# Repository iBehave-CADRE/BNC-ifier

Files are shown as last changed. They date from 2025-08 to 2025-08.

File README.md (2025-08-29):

# BNC-ifier User Guide

The BNC-ifier (Figure 1) adds I/O BNC connectors to Basler cameras, enabling simple integration into experimental imaging and behavioral setups for neuroscience. The PCB is designed to be accessible for scientists, with thorough documentation for self-assembly. Its modular design and detailed instructions allow users to adapt the PCB for any of the supported Basler cameras. A list of supported cameras with connection instructions can be found [here](https://ibehave-cadre.github.io/BNC-ifier).  A full list of parts (Table 1) and manufacturing files are provided in this repository. The BNC-ifier can be used as a stackable device or mounted in 19-inch racks.

<p align="center">
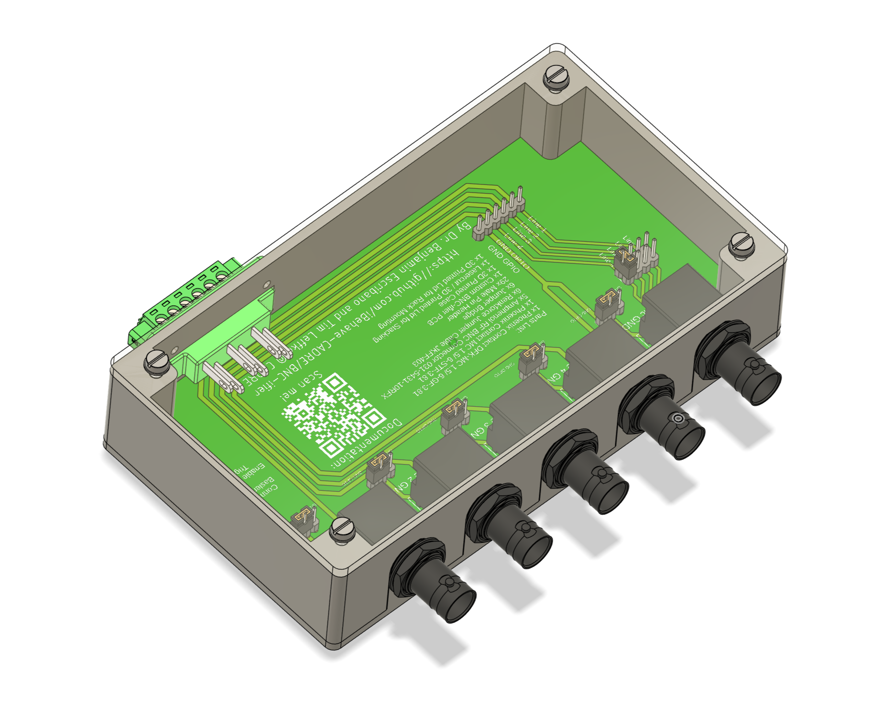
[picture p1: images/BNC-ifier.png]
  
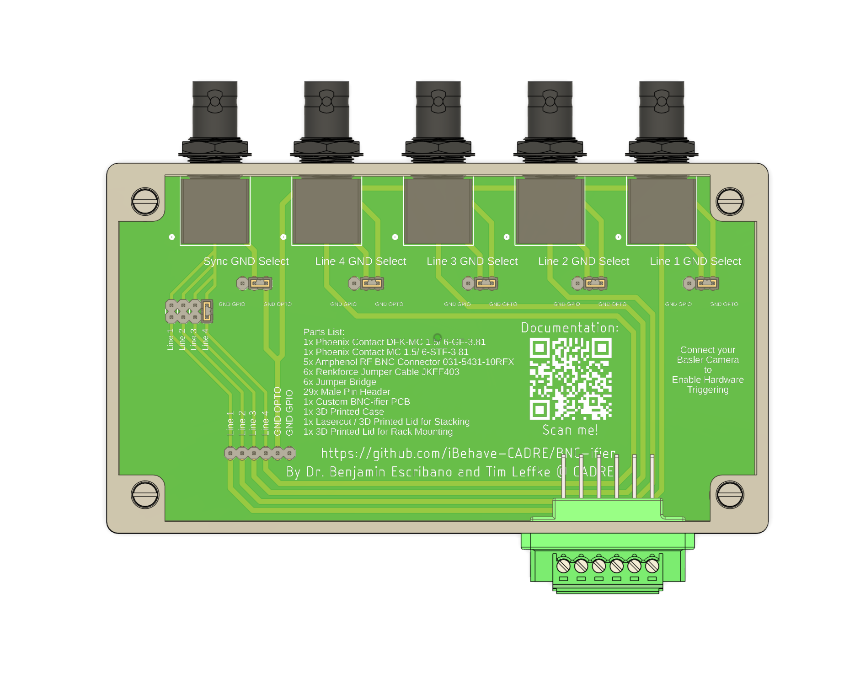
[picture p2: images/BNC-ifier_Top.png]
  
</p>

**Figure 1:** The BNC-ifier (left) and the accessible documentation with parts list, QR code for GitHub and contact details on the PCB (right).

Using this device allows synchronization of the Basler camera with microscopes, DAQs, sensors, and actuators via 5V TTL digital pulses (Figure 2). It also allows daisy-chaining Basler cameras via the sync port in order to synchronize frames between cameras. Additionally, one can grab time stamps from the sync port or one of the many BNC ports, depending on the I/O settings.

<p align="center">
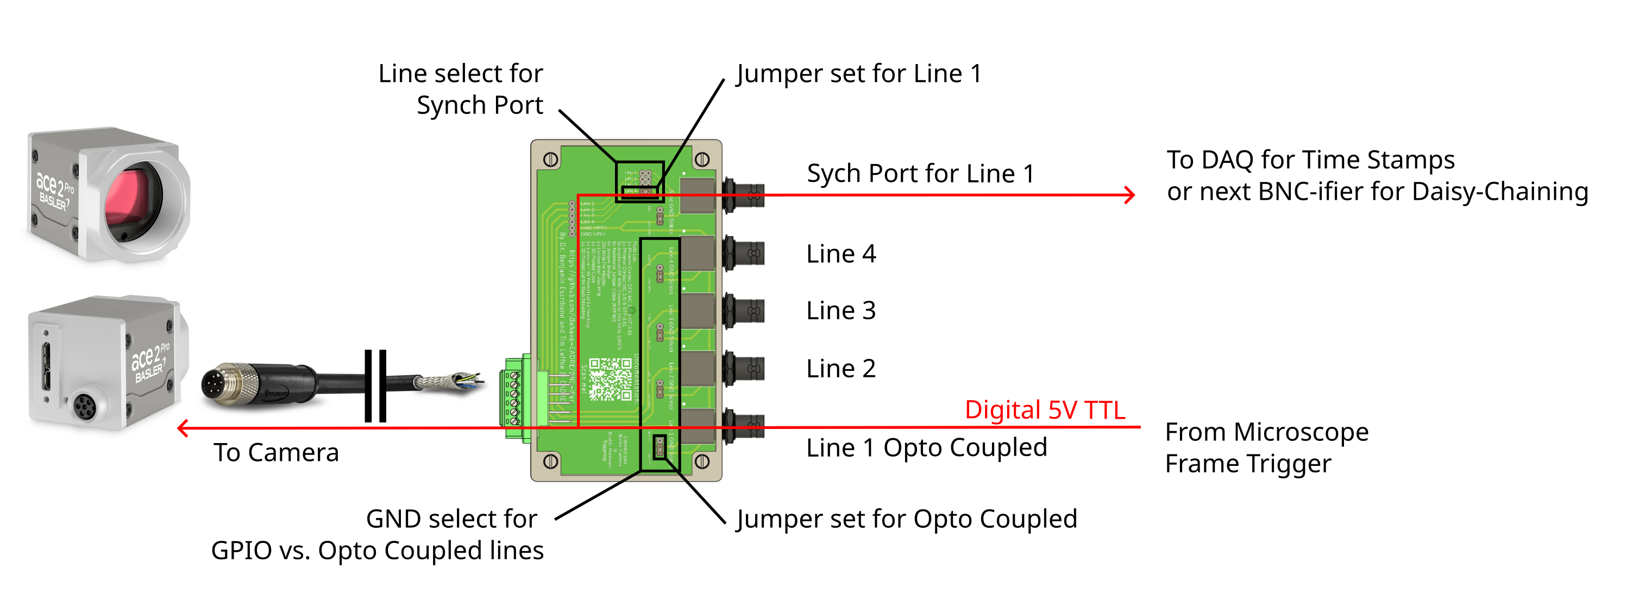
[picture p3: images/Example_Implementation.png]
  
</p>

  **Figure 2:** Schematic of exemplary implementation of the BNC-ifier. Here, a 2P-Microscope frame frigger (e.g. from ScanImage) is connected to Line 1 to trigger individual frames of the Basler camera. At the same time, the sync port is connected to a DAQ for data logging and time stamps. The image of the Basler camera and I/O cable wasobtained and adapted from [baslerweb.com](https://www.baslerweb.com/).

## Assembly

For assembling the BNC-ifier, access to a 3D printer, a laser cutter, and a soldering station are recommended. The PCB can be obtained in the CADRE Maker Space or ordered via any online manufacturer for PCBs. The commercial parts can be ordered online if not available in the CADRE Maker Space. We also provide support for sourcing all the parts and keep them in stock if possible. All parts for the case can be 3D printed in the CADRE Maker Space or ordered via online 3D printing services.

<p align="center">
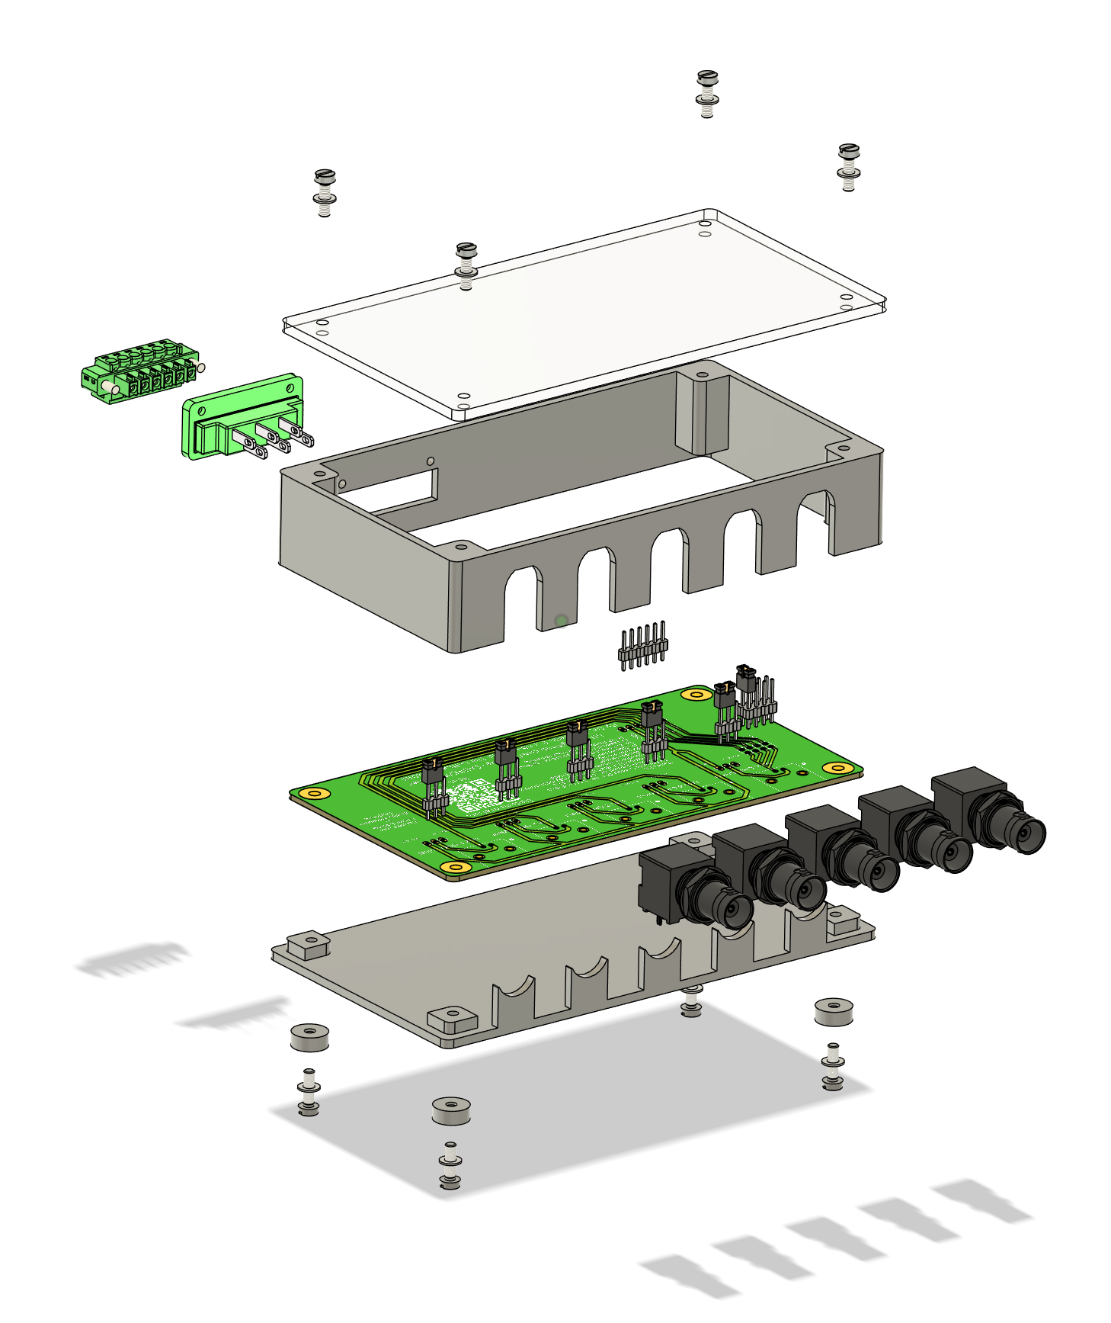
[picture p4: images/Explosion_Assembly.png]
  
</p>

**Figure 3:** Exploded view of the BNC-ifier for assembly instructions.

1. Assembling the PCB: All electronic parts have to be soldered to the top side of the PCB at the labeled positions. This includes the BNC connectors and all the male pin headers. Once all the parts are soldered, each pin terminal can be equipped with a jumper bridge. This jumper will later be used for the configuration of the BNC-ifier.

2. Preparing the Connector: The green Phoenix Contact connector has to be equipped with jumper cables. Therefore, jumper cables with female pin headers have to be soldered to the connector and finished with shrink tubing.

3. Preparing the Case: All parts of the case have to be 3D printed and laser cut. Once they are manufactured, they can be assembled with screws (Figure 3). The PCB goes in between the top and bottom parts of the case. The Phoenix Contact connector then needs to be attached to the hole, and the jumper cables need to be inserted.

5. Now the lid can be closed with the additional screws.

> [!NOTE]
> For the rack-mounted version (Figure 4), the lid needs to be closed after placing the BNC-ifier in the rack panel. Closing the lid will then secure the device in the panel.

<p align="center">
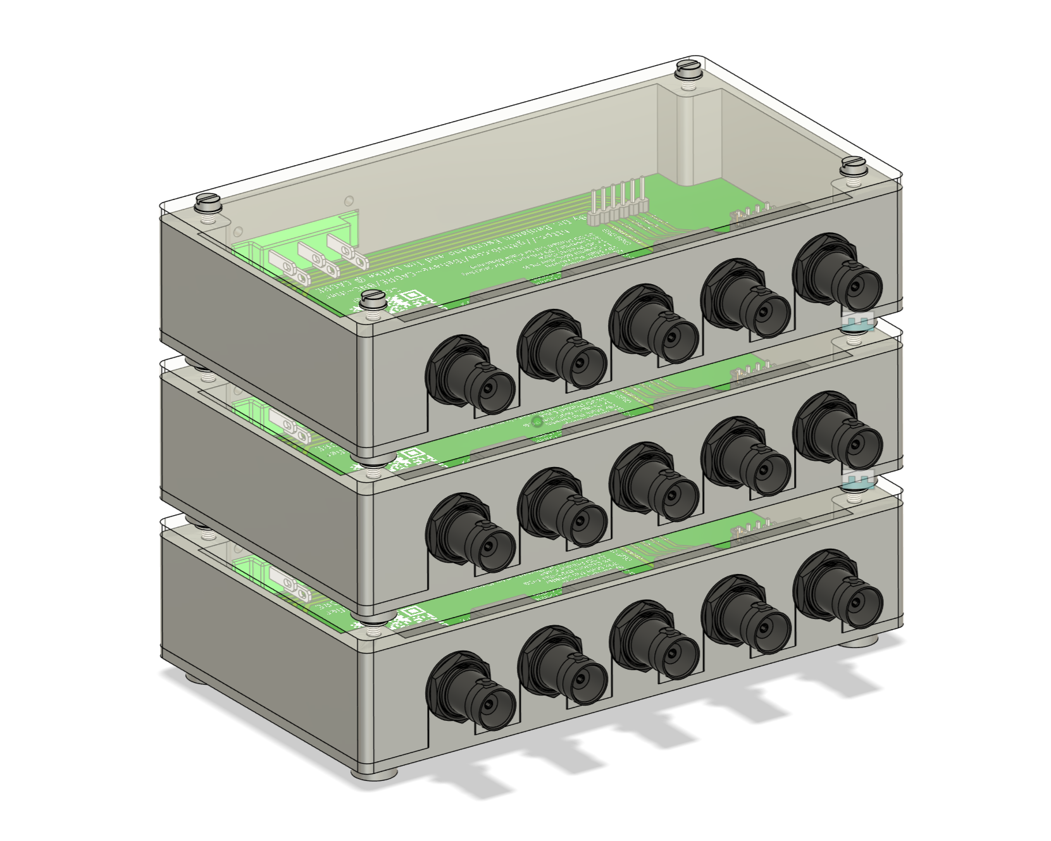
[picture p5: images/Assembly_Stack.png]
  
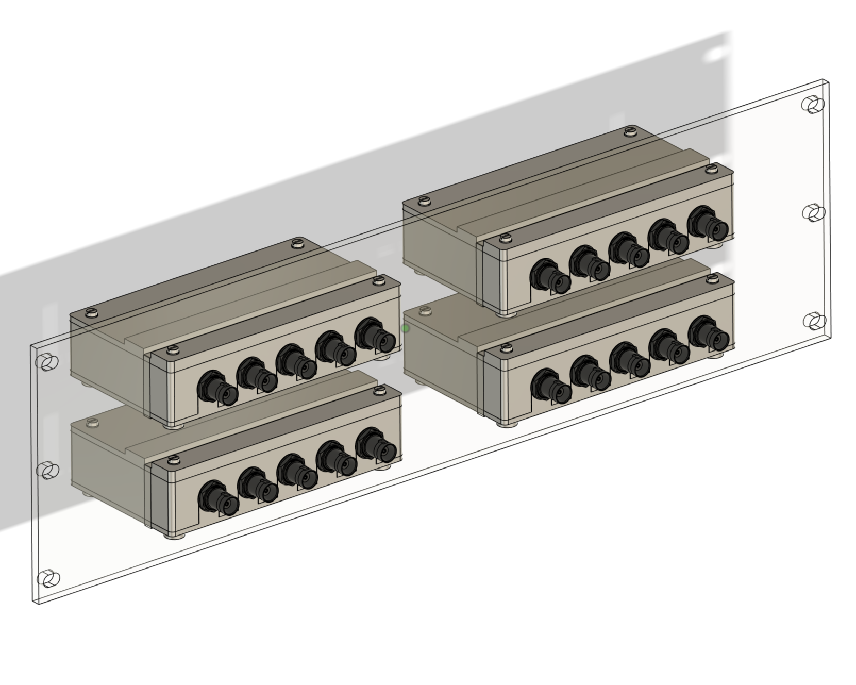
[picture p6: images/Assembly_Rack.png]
  
</p>

**Figure 4:** BNC-ifier as a stack (left) and mounted in a rack panel (right).

## Configuration of the BNC-ifier

For connecting the Basler camera to the BNC-ifier, an I/O cable with the corresponding connector for the camera on one end and open pins on the other end must be available. This cable can be ordered on the Basler web page using the following [link](https://www.baslerweb.com/en/accessories/?accessory_type=I/O+/+Power+Cable#products). Normally, the cable comes with a small piece of paper providing the color code, cable pin layout, and numbering.

> [!TIP]
> If this document was lost or not provided, the color code and pin layout of the cable can be determined with a multimeter in continuity mode. Connecting the probes to a pin of the cable connector and an open wire end of the cable will make the multimeter beep if there is electrical continuity. The pairing of beeping pins and wire colors can then be noted down.

Depending on the camera model, each I/O line can be an opto-coupled or a GPIO line, while each type has its own ground pin. Therefore, the BNC-ifier grounding scheme has to be configured in order to provide each pin with the correct reference ground.

To find out which camera pin has to be connected to which BNC-ifier pin, please refer to this [site](https://ibehave-cadre.github.io/BNC-ifier). Clicking on the camera name will provide the pin type, pin layout, and pin number of each camera, along with an illustration and table. If this site does not work, please refer to the `cameras.csv` file and the `pin_numbering` folder in this repository.

The BNC-ifier can now be configured as follows:

1. Connect each camera pin to the corresponding pin of the Phoenix Contact connector screw terminal on the BNC-ifier box.
2. Unscrew the top of the BNC-ifier and open the lid.
3. Each jumper cable can now be connected to the corresponding line on the 6x male pin header terminal.
3. The jumper bridges on the 3x male pin headers can now be placed to select the corresponding ground (opto-coupled vs. GPIO) for Lines 1-4.

> [!TIP]
> If there is no ground (GND) for the line in the table, it does not matter how the pin header is set.

4. To configure the sync port, the jumper bridge can be placed to select one of the four lines on the 2x4 male pin header. This will allow output of any signal on the selected line to the sync BNC port in a bidirectional manner.
5. Place the lid back on the BNC-ifier and screw it on.

## Integration in Experimental Setups

The BNC-ifier can now be connected to other devices via coaxial BNC cables. Lines 1-4 can be configured in Pylon in order to start camera frames, provide information like exposure time or timestamps, and much more. The sync port can also be used for recording timestamps via a DAQ, but if connected to Lines 1-4 of another camera, it acts as a daisy-chaining port. The provided wiring diagram (Figure 5) and PCB layout (Figure 6) can help to understand the BNC-ifier and plan its setup integration.

## References and Contact Details

The BNC-ifier is used by the laboratories of Sabine Krabbe (DZNE, Bonn), Tobias Rose (IEECR, Bonn), Tobias Ackels (IEECR, Bonn), Ilona Grunwald-Kadow (Institute for Physiology, Bonn), and many more to come...

For any further questions, please contact the [CADRE Team](https://ibehave.nrw/ibots-platform/cadre/)

## Wiring Diagram

<p align="center">
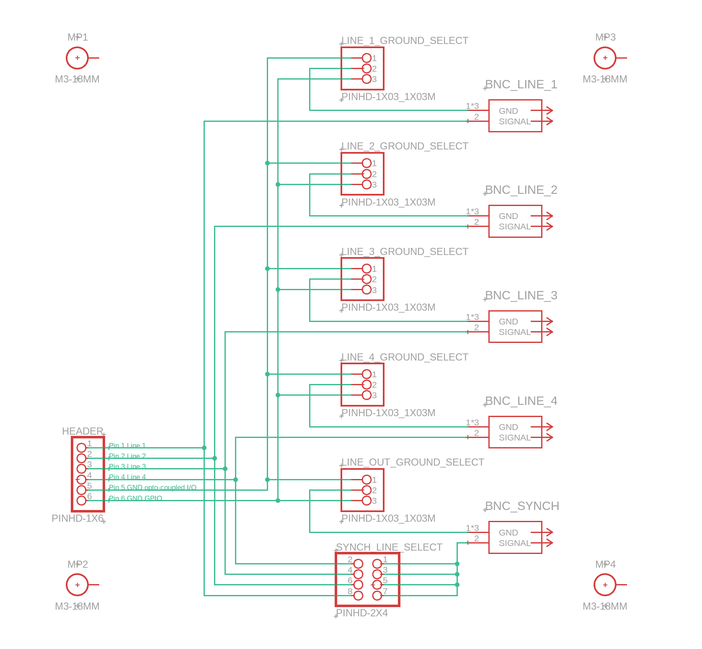
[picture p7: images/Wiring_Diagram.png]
  
</p>

**Figure 5:** Schematics of electronics circuit of the BNC-fier.

## PCB Layout

<p align="center">
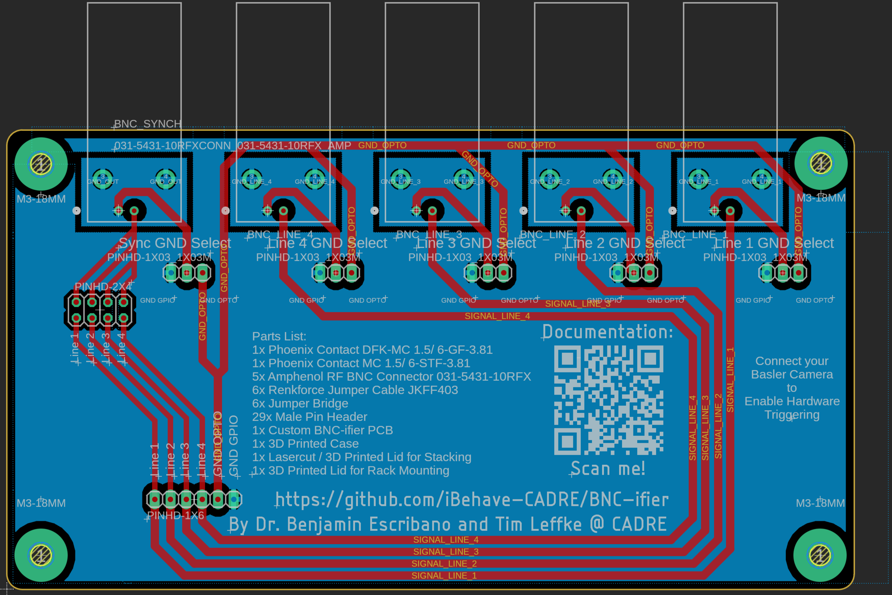
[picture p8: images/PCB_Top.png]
  
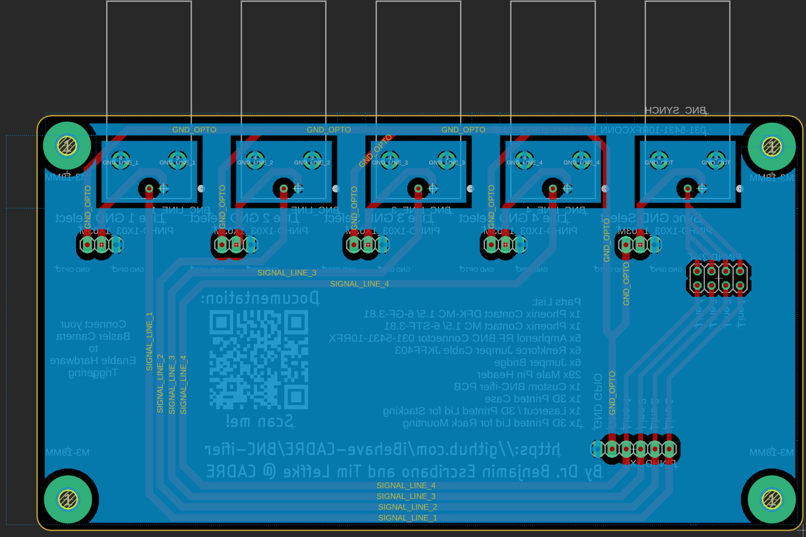
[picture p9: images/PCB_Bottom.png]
  
</p>

**Figure 6:** PCB layout of the BNC-ifier from top (left) and bottom (right).

## Parts List

| Item | Quantity | Notes | Product Example Link |
| :--- | :---: | :---: | :---: |
|  |  |  |  |
| **Commercial Parts:** |
|  |  |  |  |
| Custom BNC-ifier PCB | 1 piece | [custom design](PCB) | [eurocircuits.com](https://www.eurocircuits.com/) |
| Phoenix Contact DFK-MC 1.5/ 6-GF-3.81 | 1 piece | |[rs-online.com](https://uk.rs-online.com/web/p/pluggable-terminal-blocks/1761449?gb=s)|
| Phoenix Contact MC 1.5/ 6-STF-3.81 | 1 piece ||[rs-online.com](https://uk.rs-online.com/web/p/pluggable-terminal-blocks/1703921?gb=s)|
| Amphenol RF BNC Connector 031-5431-10RFX | 5 pieces ||[rs-online.com](https://uk.rs-online.com/web/p/coaxial-connectors/1440890?gb=a)|
| Renkforce Jumper Cable JKFF403 | 6 pieces ||[rs-online.com](https://www.conrad.de/de/p/renkforce-jkff403-jumper-kabel-arduino-banana-pi-raspberry-pi-40x-drahtbruecken-buchse-40x-drahtbruecken-buchse-30-2299845.html)|
| Jumper Bridge | 6 pieces ||[rs-online.com](https://de.rs-online.com/web/p/jumper/7636776P?gb=s)|
| Male Pin Header | 29 pieces ||[rs-online.com](https://de.rs-online.com/web/p/leiterplatten-header/2518632?gb=s)|
| Shrink Tube | 16 pieces of 1.5 cm ||[rs-online.de](https://de.rs-online.com/web/p/warmeschrumpfschlauche/2833249?gb=s)|
| Screw M3x10 Flathead | 8 pieces | self-tapping|[mercateo.com](https://www.mercateo.com/p/1498C-8000152817/Flachkopfschraube_DIN_85_ISO_1580_Schlitz_M3x10_4_8_galv_verz_200St_.html?ViewName=live~secureMode)|
| Washer M3 | 8 pieces | |[mercateo.com](https://www.mercateo.com/p/4502-16H900/Unterlegscheibe_M3_H_0_5_mm_Aussen_7_mm_Stahl_verzinkt_DIN_125_ISO_7090_.html?ViewName=live~secureMode)|
|  |  |  |  |
| **Parts for Case:** |
|  |  |  |  |
| Case Frame Top | 1 piece | [custom design](Case/Case_Frame_Top.stl) | 3D printed |
| Case Frame Bottom | 1 piece | [custom design](Case/Case_Frame_Bottom.stl) | 3D printed |
|  |  |  |  |
| **Parts for Stacking Case:** |
|  |  |  |  |
| Top Lid Stackable | 1 piece | [custom design](Case/Top_Lid_Stackable.stl) | lasercut, can be printed |
| Stacking Feet | 4 pieces | [custom design](Case/Stacking_Feet.stl) | 3D printed |
|  |  |  |  |
| **Parts for Rack Mounting Case:** |
|  |  |  |  |
| Rack Mounting Case Top Back | 1 piece | [custom design](Case/Rack_Mounting_Case_Top_Back.stl) | 3D printed |
| Rack Mounting Case Top Front | 1 piece | [custom design](Case/Rack_Mounting_Case_Top_Front.stl) | 3D printed |
| Rack Panel | 1 piece | [custom design](Case/Rack_Panel.stl) | lasercut |

**Table 1:** Parts list for building BNC-fier either as stackable device or for mounting in a 19 inch rack.

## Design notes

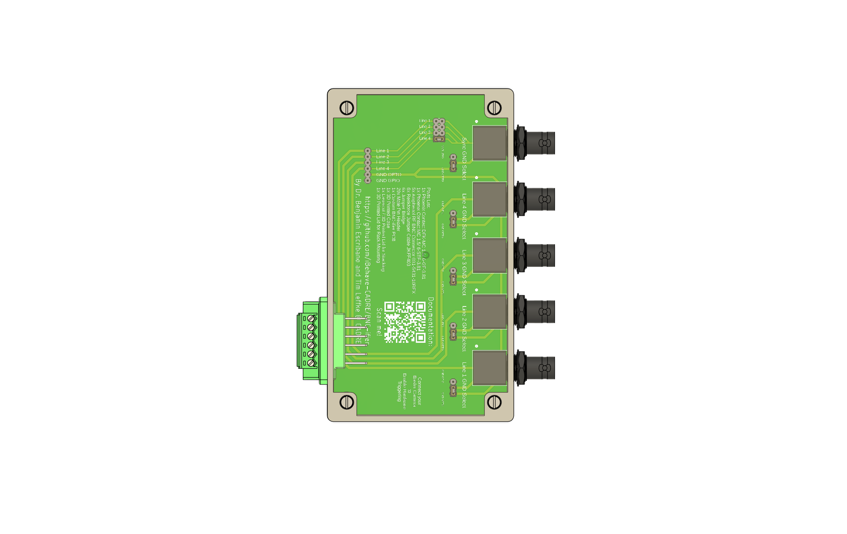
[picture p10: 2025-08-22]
images/Screenshot 2025-08-22 134631.png

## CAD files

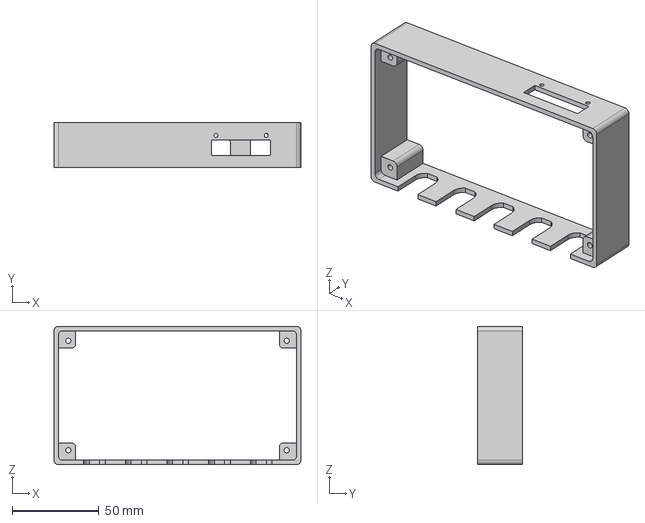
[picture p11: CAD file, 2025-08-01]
Case/Case_Frame_Top.step
142.2 x 26.0 x 79.5 mm

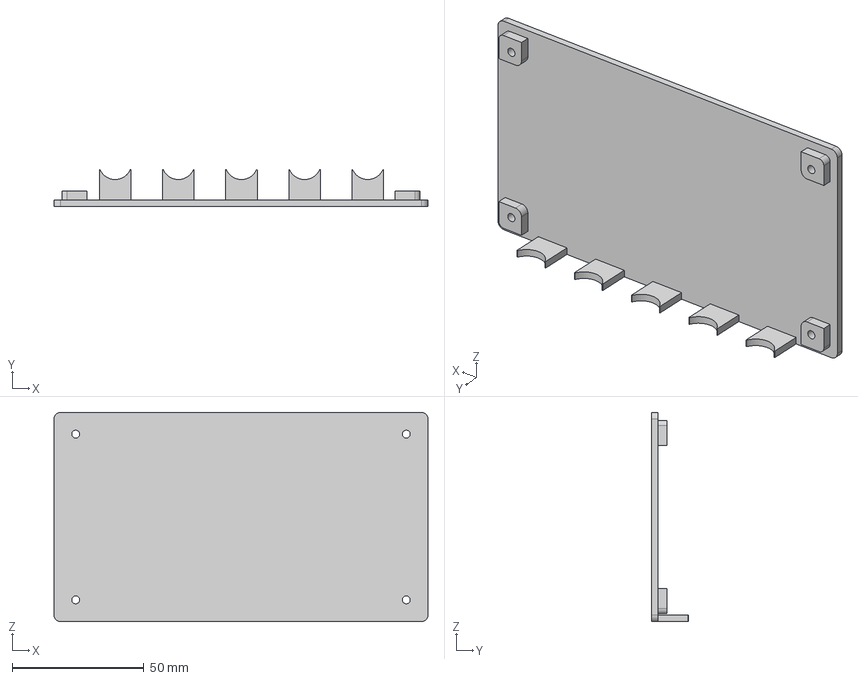
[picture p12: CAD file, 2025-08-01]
Case/Case_Frame_Bottom.step
142.2 x 14.1 x 79.5 mm

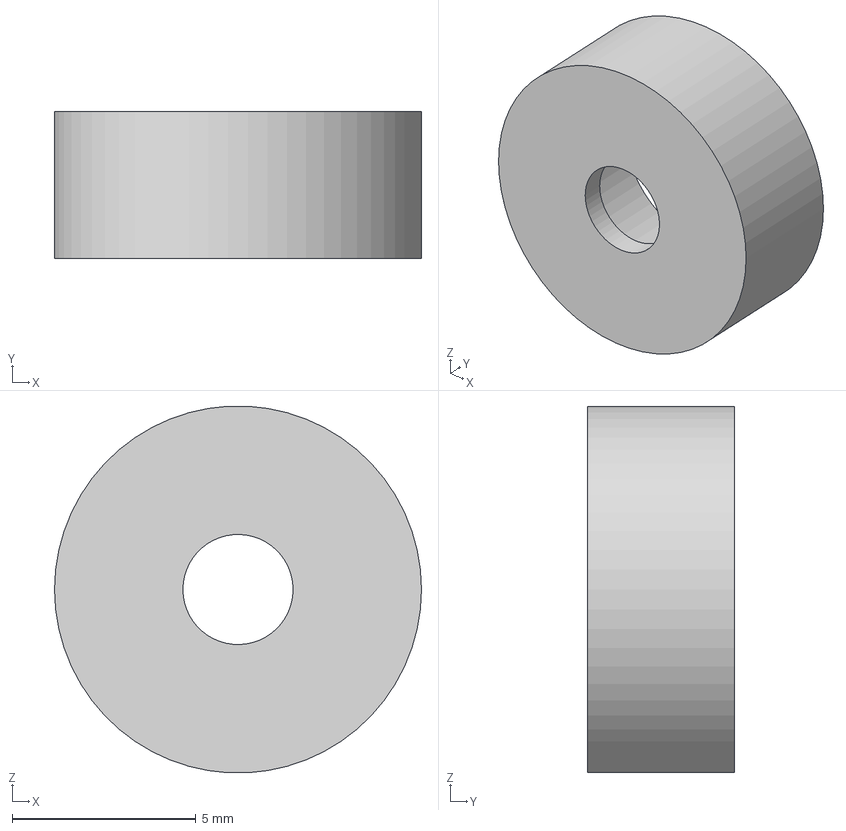
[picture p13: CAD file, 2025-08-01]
Case/Stacking_Feet.step
10.0 x 4.00 x 9.99 mm

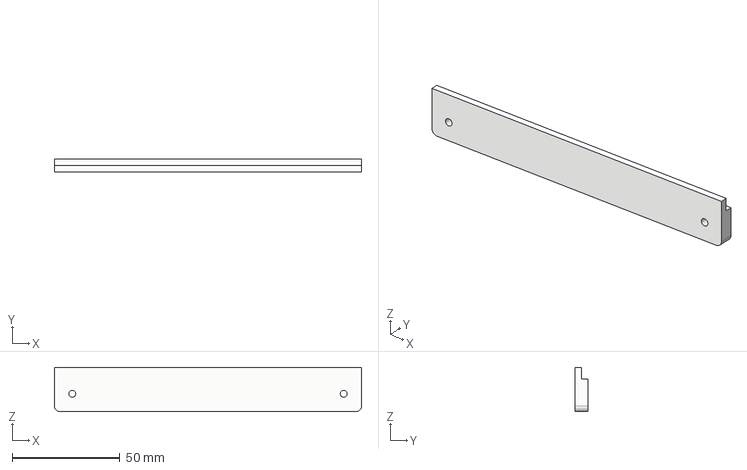
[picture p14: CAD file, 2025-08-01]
Case/Rack_Mounting_Case_Top_Front.step
142.2 x 6.00 x 20.5 mm

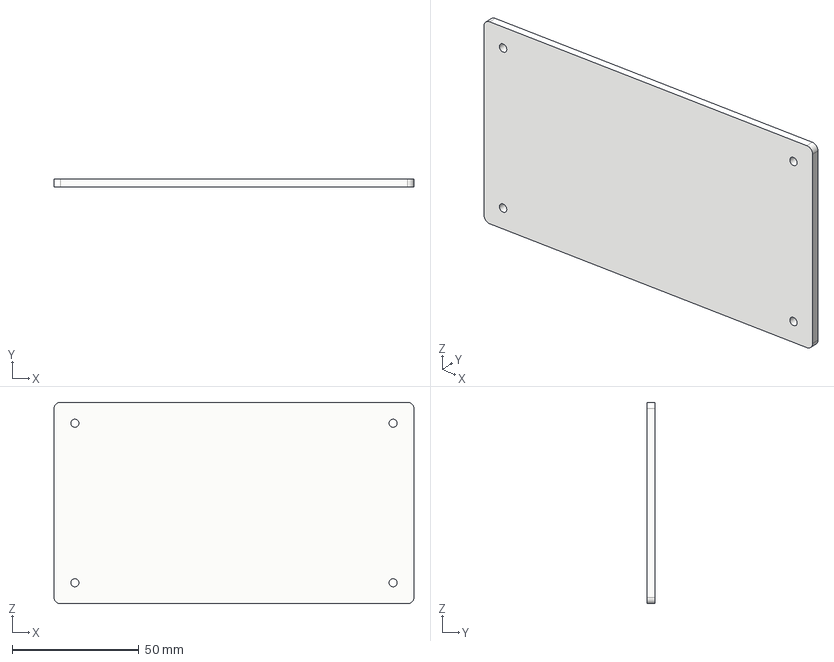
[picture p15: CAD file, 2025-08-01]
Case/Top_Lid_Stackable.step
142.2 x 3.00 x 79.5 mm

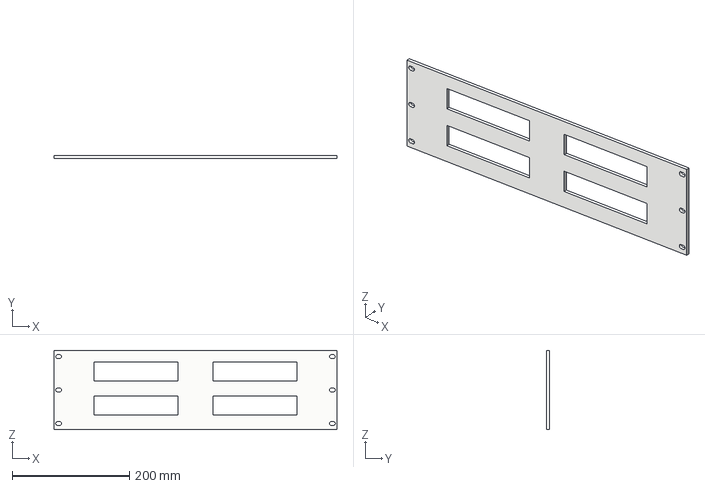
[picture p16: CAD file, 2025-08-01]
Case/Rack_Panel.step
483.4 x 5.00 x 135.0 mm

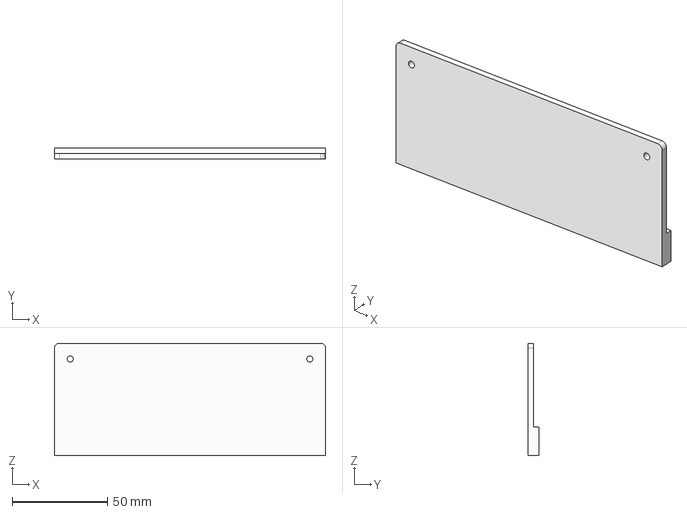
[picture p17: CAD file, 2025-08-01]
Case/Rack_Mounting_Case_Top_Back.step
142.2 x 6.00 x 59.0 mm

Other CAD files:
Case/Case_Frame_Bottom.stl
Case/Case_Frame_Top.stl
Case/Rack_Mounting_Case_Top_Back.stl
Case/Rack_Mounting_Case_Top_Front.stl
Case/Rack_Panel.dxf
Case/Rack_Panel.stl
Case/Stacking_Feet.stl
Case/Top_Lid_Stackable.dxf
Case/Top_Lid_Stackable.stl

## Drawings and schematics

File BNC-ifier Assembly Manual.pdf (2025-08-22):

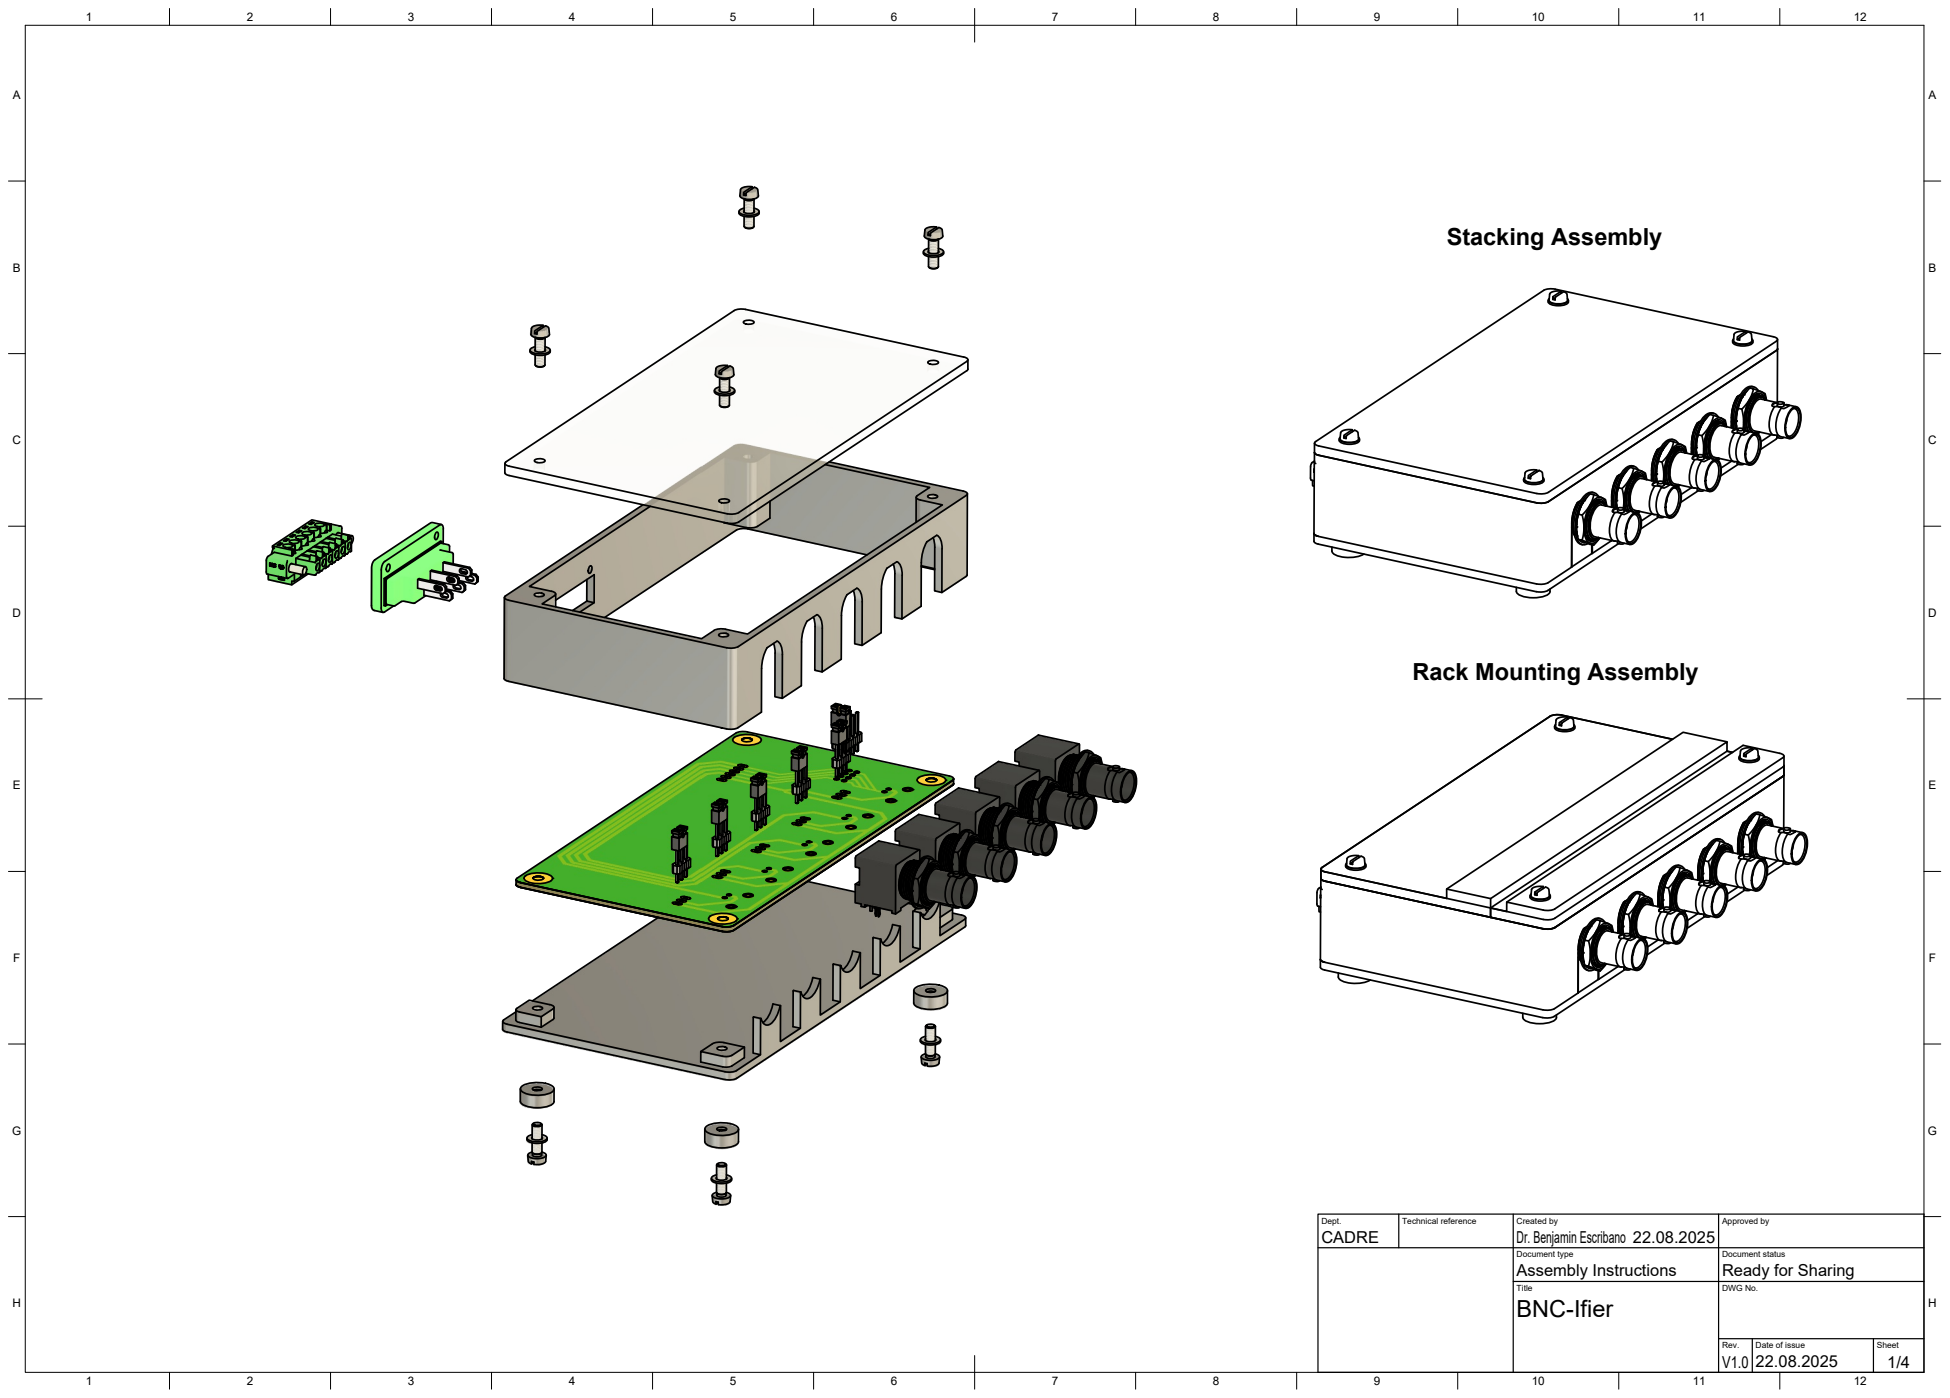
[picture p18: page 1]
Stacking Assembly

Rack Mounting Assembly

Dept. CADRE | Technical reference | Created by Dr. Benjamin Escribano 22.08.2025 | Approved by

Document type Assembly Instructions | Document status Ready for Sharing

Title BNC-Ifier | DWG No.

Rev. V1.0 | Date of issue 22.08.2025 | Sheet

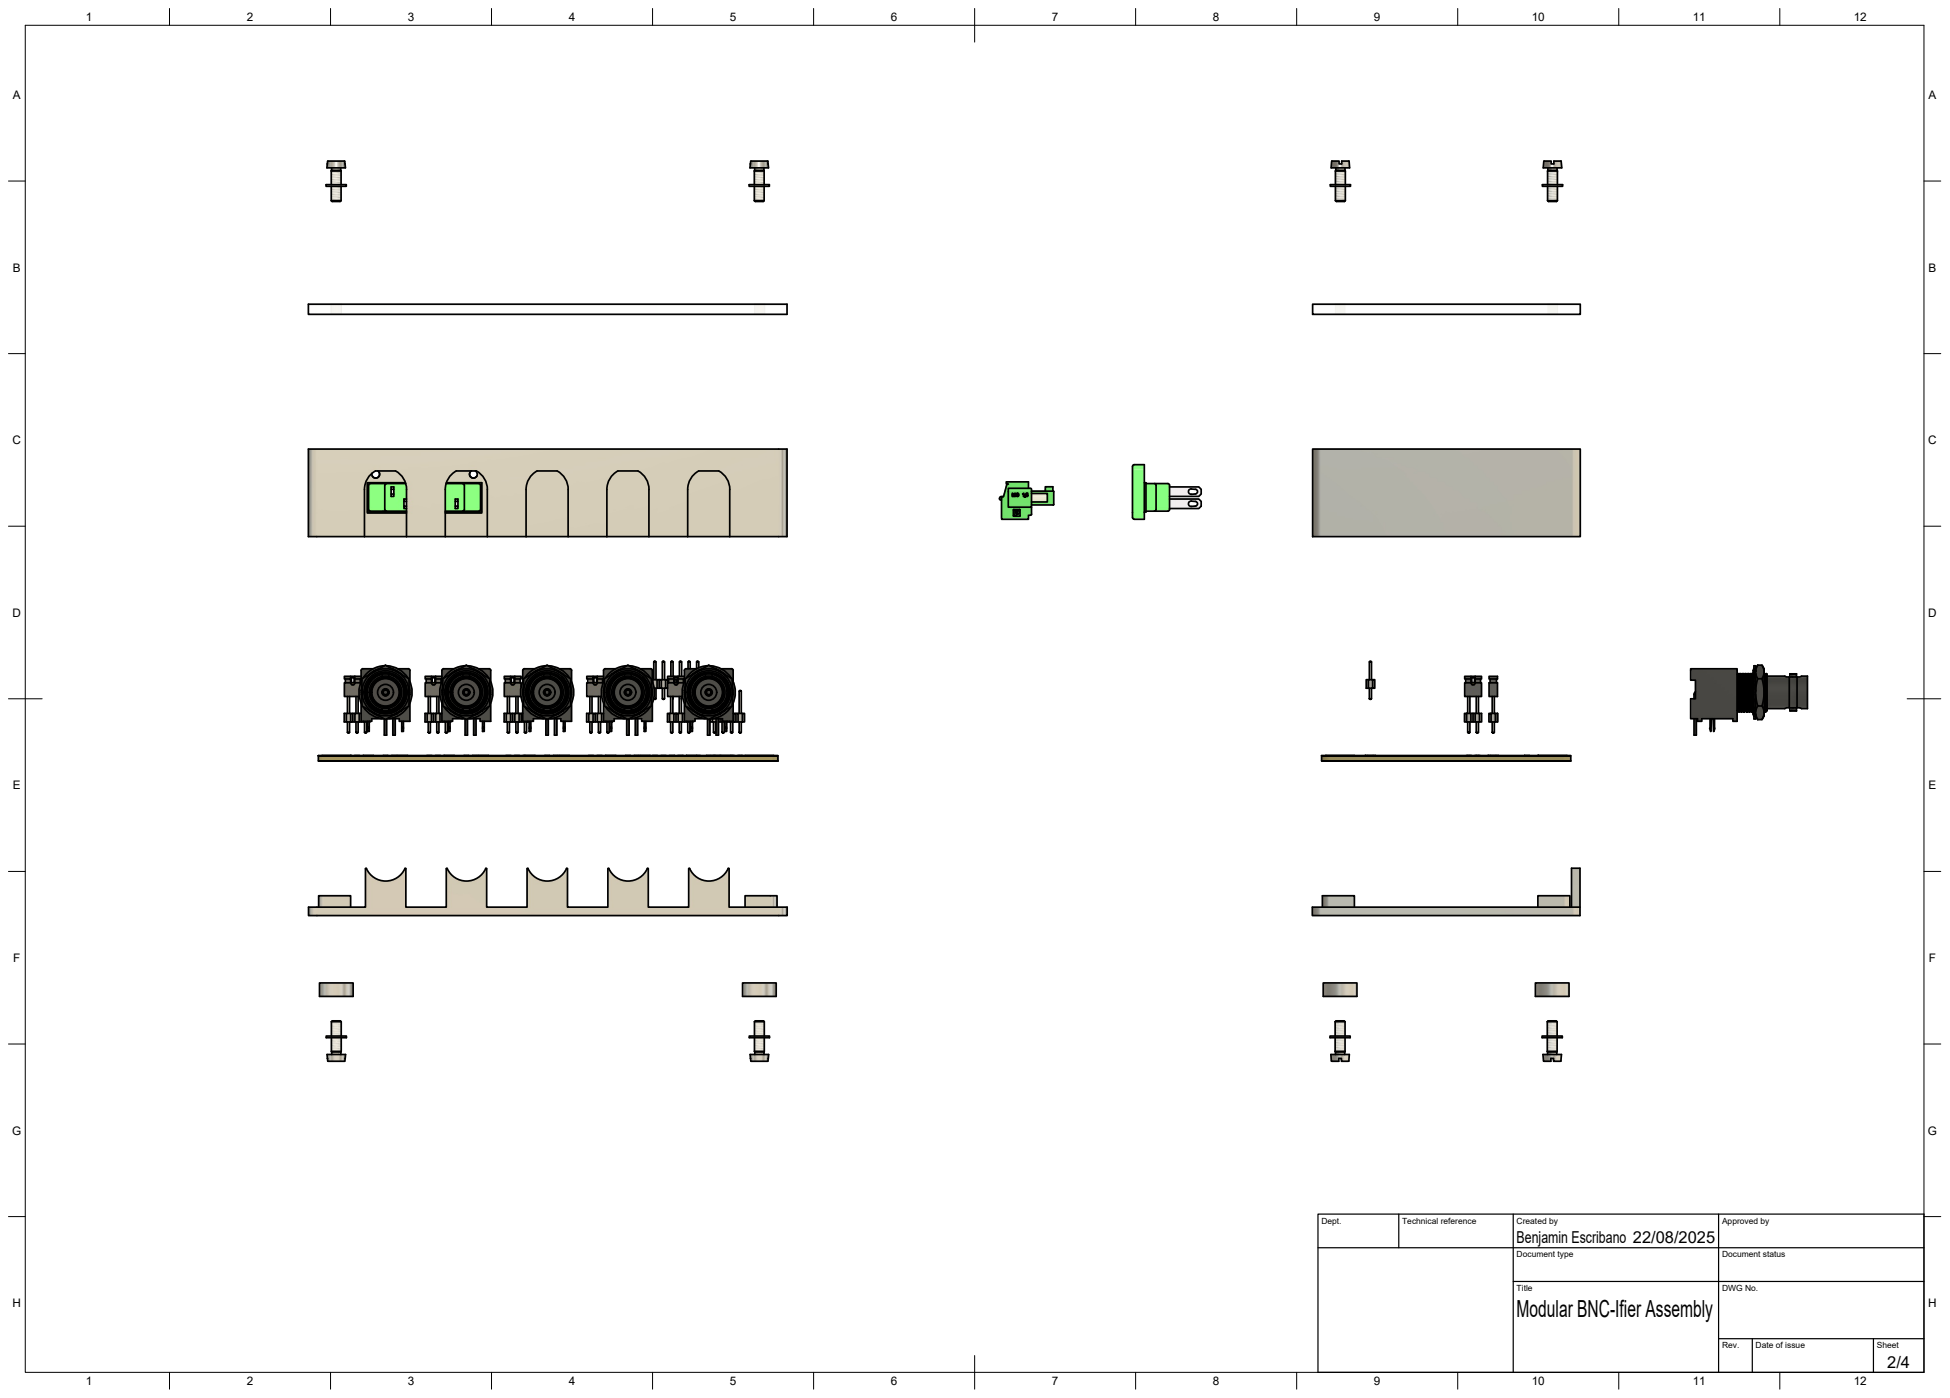
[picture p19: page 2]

Dept. | Technical reference | Created by Benjamin Escribano 22/08/2025 | Approved by

Document type | Document status

Modular BNC-Ifier Assembly

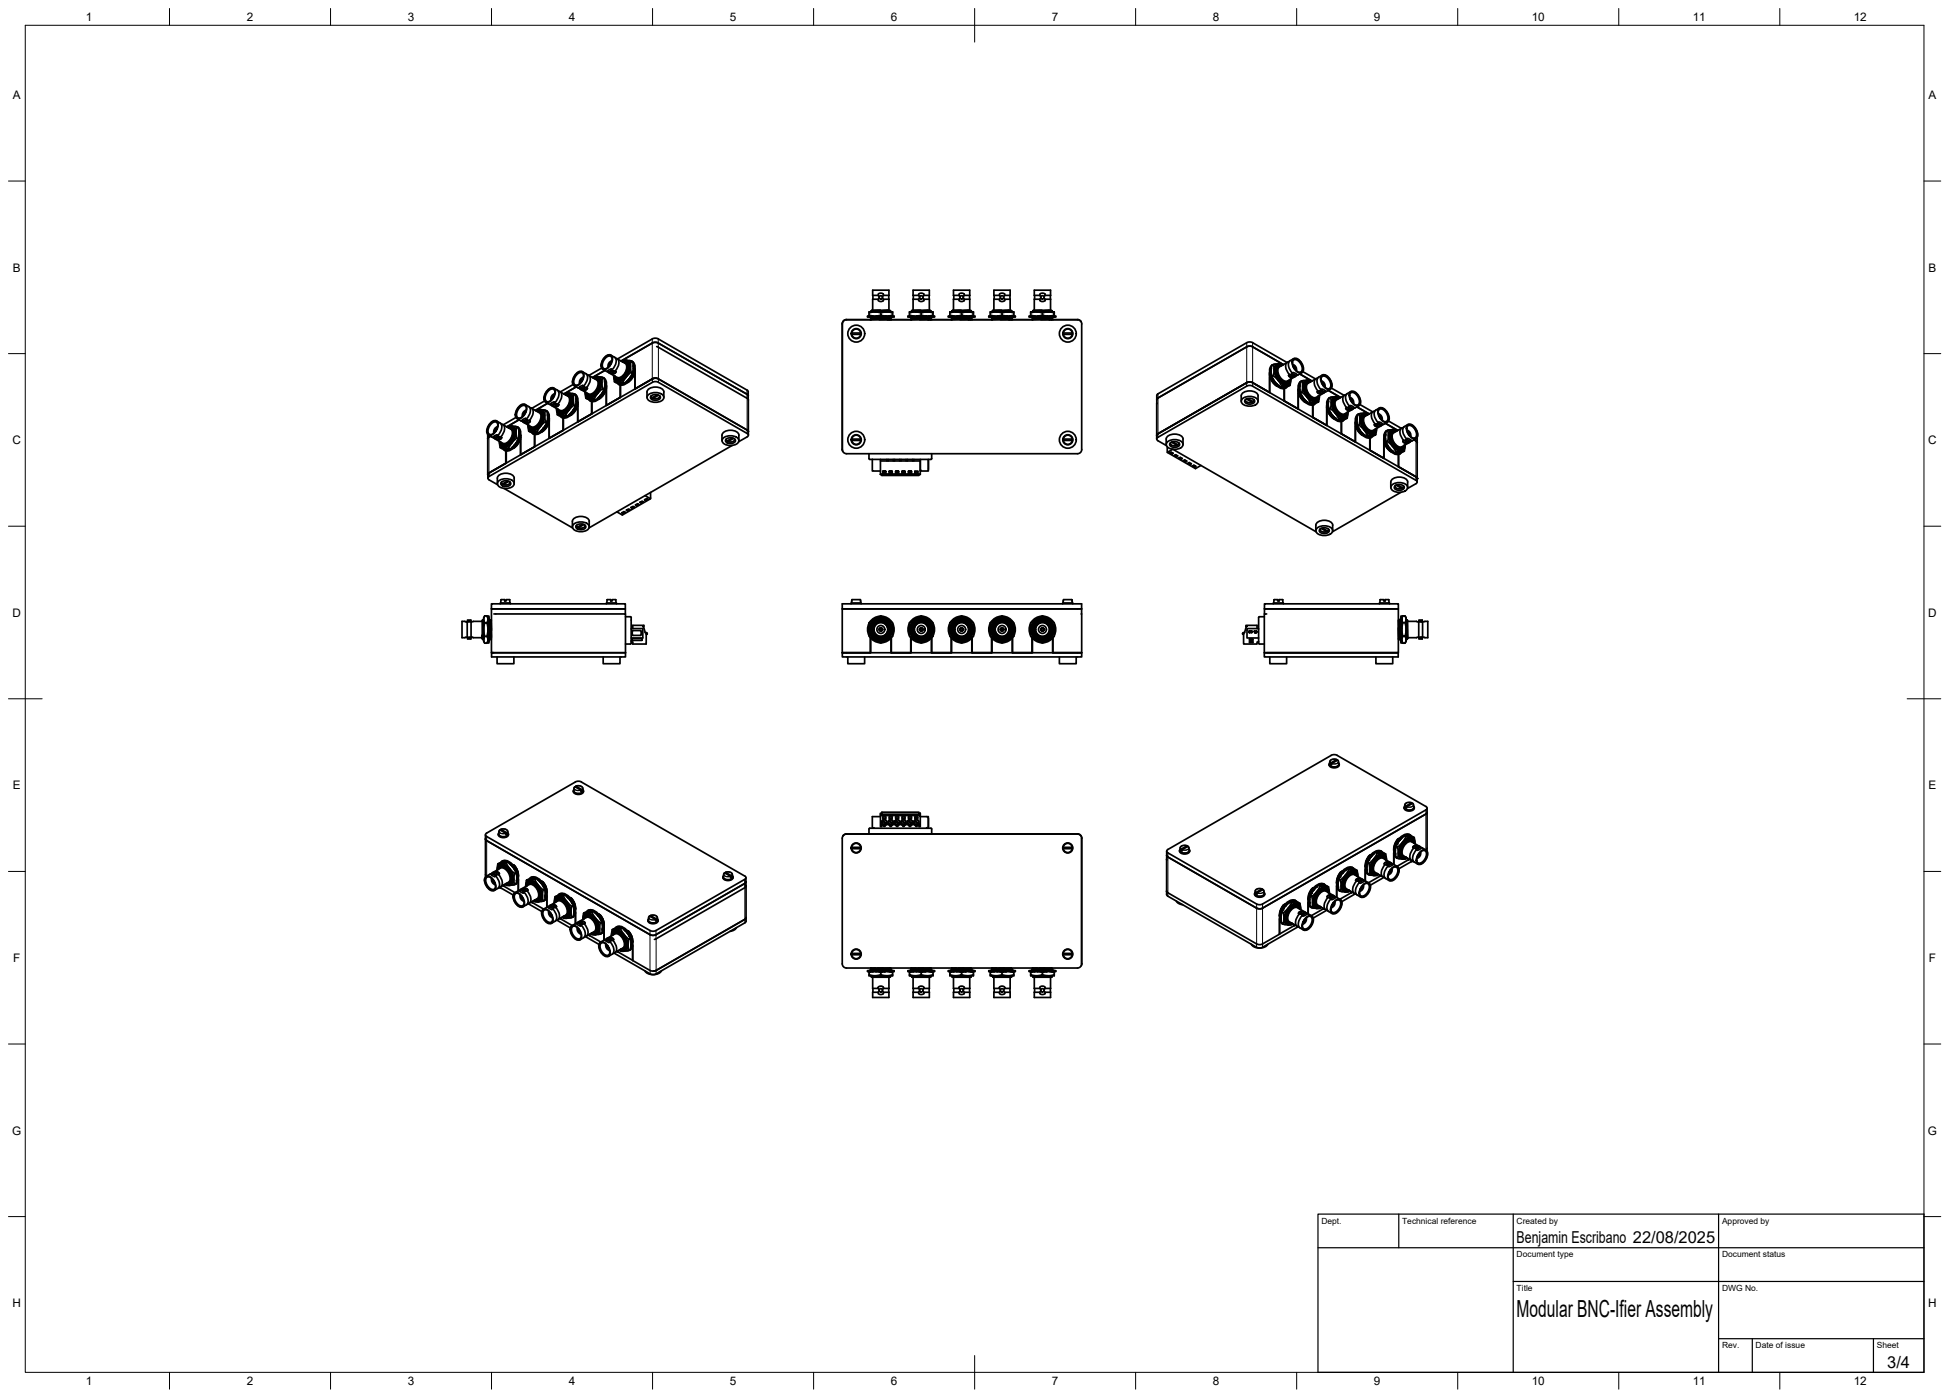
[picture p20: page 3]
Dept.; Technical reference; Created by; Approved by; Document type; Document status; Benjamin Escribano

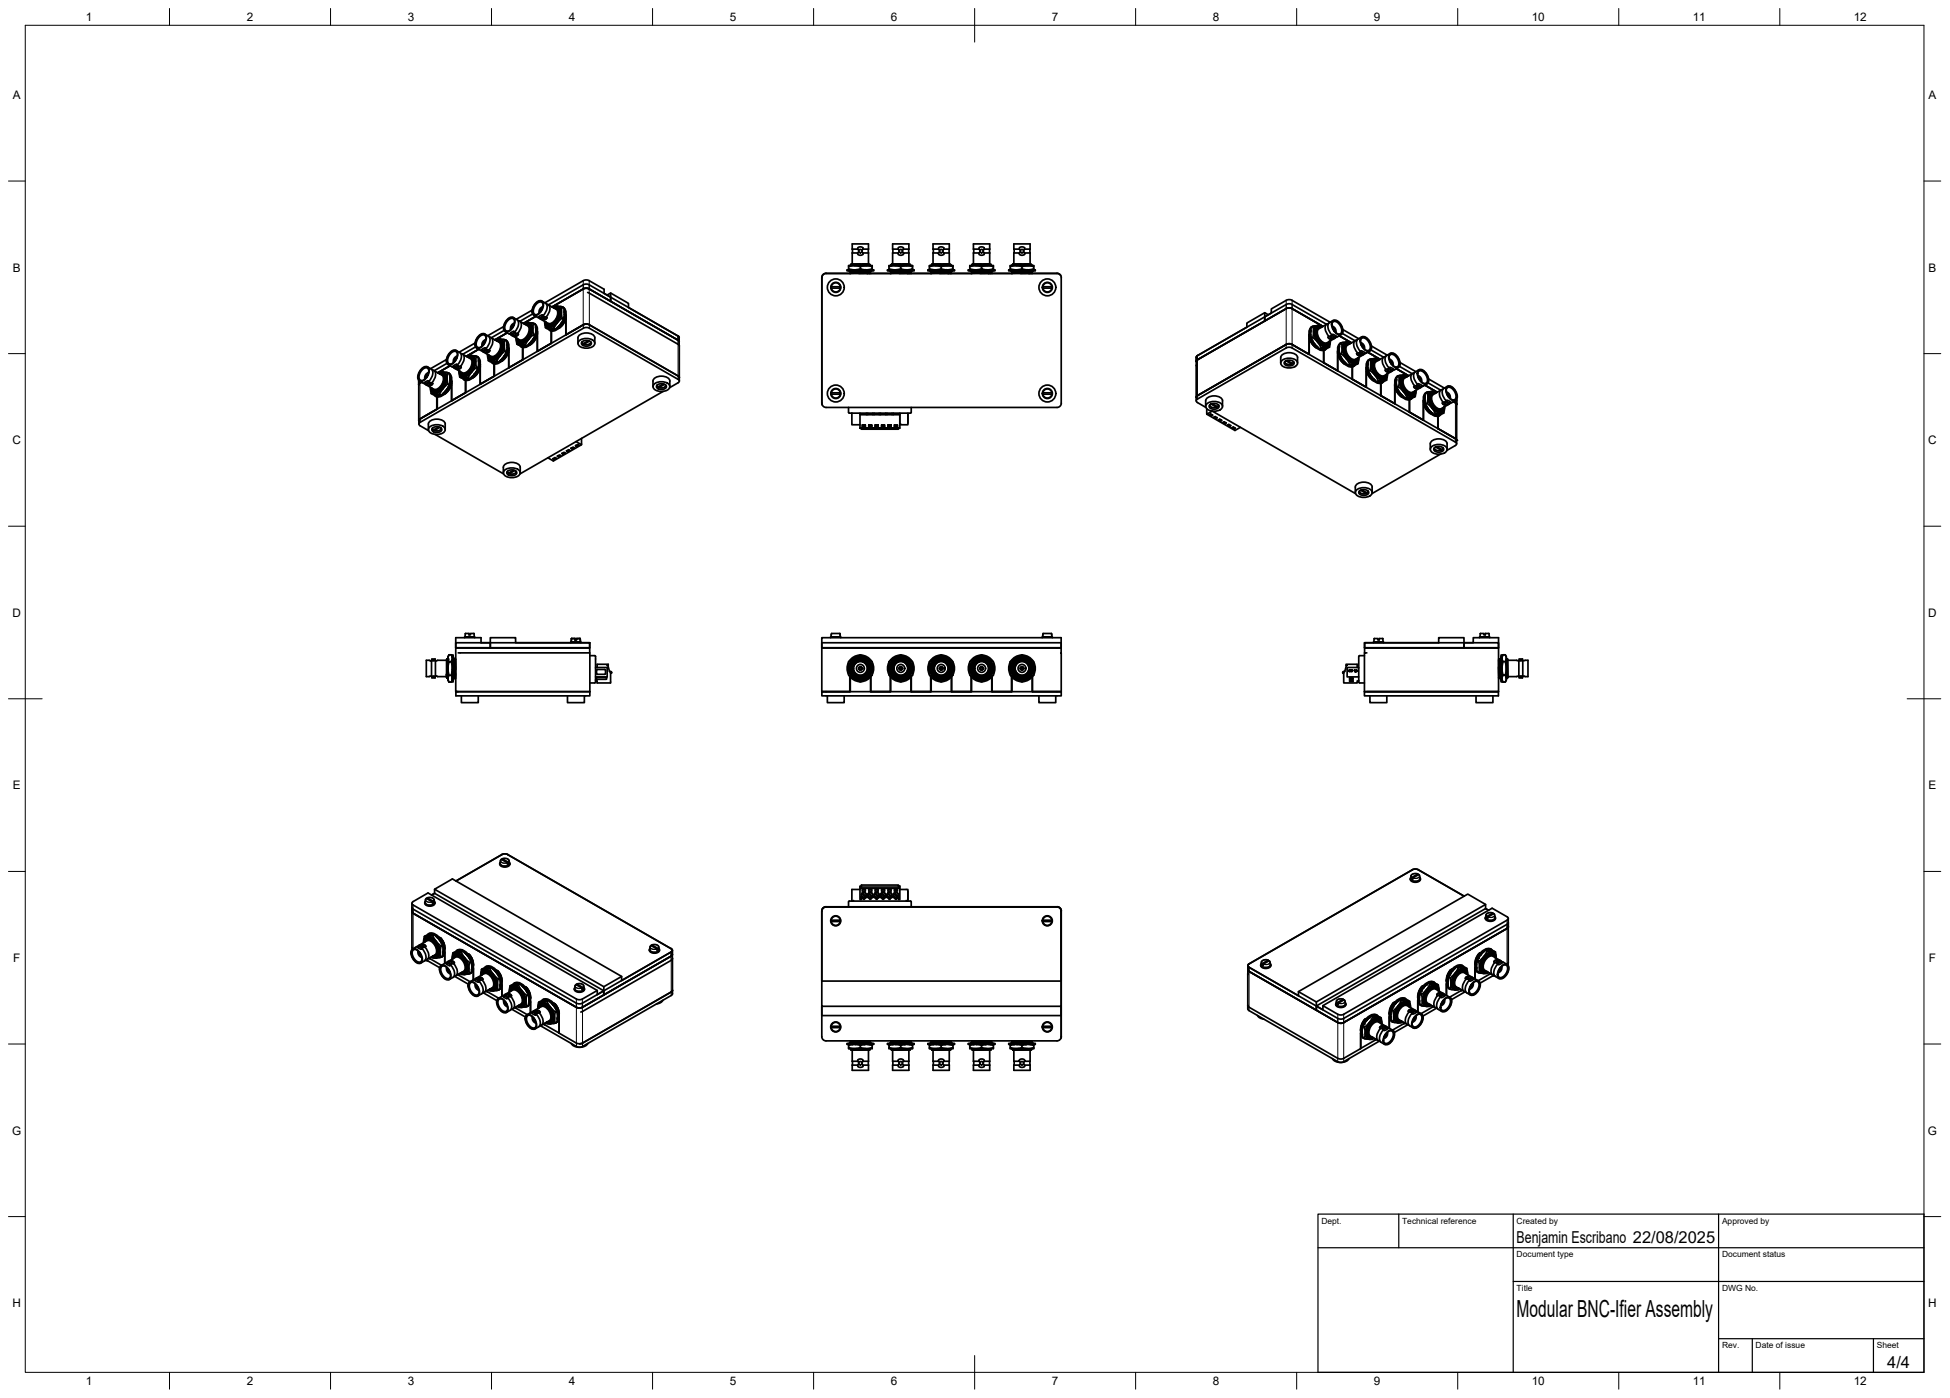
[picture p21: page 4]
Dept.; Technical reference; Created by; Approved by; Document type; Document status; Benjamin Escribano

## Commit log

2025-03-18 Upload of pin numbering Batch #1
2025-03-18 Upload of pin numbering Batch #2
2025-03-18 Upload of pin numbering Batch #3
2025-03-18 Upload of pin numbering Batch #4
2025-04-01 Added numbered pin images
2025-04-01 initial upload
    [cameras.csv]
2025-04-08 Added link to basler for cameras
2025-04-08 Added cursor to result items
    When hovering over the cameras the mouse now becomes a cursor to indicate that you can click on them
2025-04-11 Added website to guide
    Additionally I took the long table out of the README, since it now can be found in the cameras.csv file
2025-08-01 Manufacturing Files
    [BNC-Ifyer_PCB.brd, Case_Frame_Bottom.step, Case_Frame_Bottom.stl, Case_Frame_Top.step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]
2025-08-22 Assembly Manual PDF
